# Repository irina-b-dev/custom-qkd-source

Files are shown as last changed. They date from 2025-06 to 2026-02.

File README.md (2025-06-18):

# custom-qkd-source

### On **Pi A** (set IP `192.168.2.1/24`):

Create a file:

```bash
sudo nano /etc/systemd/network/10-eth0.network
```

```ini
[Match]
Name=eth0

[Network]
Address=192.168.2.1/24
```

 Enable `systemd-networkd`:

```bash
sudo systemctl enable systemd-networkd
sudo systemctl restart systemd-networkd
```

Repeat similar steps on **Pi B**, but with a different address:

---

### On **Pi B** (set IP `192.168.2.2/24`):

```bash
sudo nano /etc/systemd/network/10-eth0.network
```

```ini
[Match]
Name=eth0

[Network]
Address=192.168.2.2/24
```

Then:

```bash
sudo systemctl enable systemd-networkd
sudo systemctl restart systemd-networkd
```

---

###  test:

```bash
ping 192.168.2.2  # from Pi A
ping 192.168.2.1  # from Pi B
```

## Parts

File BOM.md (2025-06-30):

## Optics

| Name                      | Link                                                                                                                                                 | Price   | Description                      | QTY | Code     | Check |
| ------------------------- | ---------------------------------------------------------------------------------------------------------------------------------------------------- | ------- | -------------------------------- | --- | -------- | ----- |
| Laser Detection card      | https://eksmaoptics.com/oem-dpss-lasers-diode-laser-modules/laser-accessories/laser-detection-cards/                                                 | 79 EUR  | 400-640 nm + 800-1700 nm         | 2   | 990-0846 | [x]   |
| Polarizing beam splitters | https://eksmaoptics.com/optical-components/polarizing-optics/cube-polarizing-beamsplitters/?listtype=search&searchparam=polarizing%20beam%20splitter | 135 EUR | 780nm Rs>99.5% Tp>95% 10 x 10 mm | 1   | 430-0102 | [x]   |
| BBO Crystal               | https://eksmaoptics.com/nonlinear-and-laser-crystals/nonlinear-crystals/beta-barium-borate-bbo-crystals-bbo-604h/                                    | 390 EUR | Type 1<br>P/P@400-800 nm         | 1   | BBO-604H | [x]   |
|                           |                                                                                                                                                      |         |                                  |     |          |       |

| Name                       | Link                                                                                       | Price   | Description                                        | Qty | Code | Check |
| -------------------------- | ------------------------------------------------------------------------------------------ | ------- | -------------------------------------------------- | --- | ---- | ----- |
| Safety Glasses             | https://www.edmundoptics.com/p/arg-lasershield-safety-comfort-glasses/41416/               | 141 EUR | D LB7 + IR LB4 @ 180-315nm, DIRM LB6 S @ 315-532nm | 1   |      | []    |
| IR Filter                  | https://www.edmundoptics.com/p/5mm-diameter-optical-cast-plastic-ir-longpass-filter/41541/ | 11 EUR  |                                                    | 2   |      | [x]   |
| Quarter Wave Plate<br><br> | https://www.edmundoptics.com/p/25mm-dia-4-retarder-film-wp140he/50157/                     | 16 EUR  | Polymer 25mm Dia., λ/4 Retarder Film               | 2   |      | [x]   |
| Half Wave Plate            | https://www.edmundoptics.com/p/25mm-dia-2-retarder-film-wp280/50160/                       | 16 EUR  | 25mm Dia., λ/2 Retarder Film                       | 2   |      | [x]   |
https://www.edmundoptics.com/Account/OrderHistory/Print/493222

| Name                 | Link                                                                             | Price   | Qty | Description                                                 | Code   | Check |
| -------------------- | -------------------------------------------------------------------------------- | ------- | --- | ----------------------------------------------------------- | ------ | ----- |
| 405nm Laser Diode    | https://ampul.eu/ro/diode-laser-module/2650-dioda-laser-405nm-20mw-diametru-56mm | 22,76 € | 3   | 405 nm, 20 mW, Ø5.6 mm, B Pin Code, Laser Diode             | AM2680 | [x]   |
| Alignemt laser 650nm | https://ampul.eu/en/laser-diodes-modules/2181-laser-module-5mw-650nm-dot         | 7.82 €  | 3   | Light color: Red<br>Wavelength: 650 nm<br>Performance: 5 mW | AM1232 | []    |
Total: 91 EUR
Needed (38 EUR)

| Name | Link                                                 | Price   | Qty | Description            | Code             | Check |
| ---- | ---------------------------------------------------- | ------- | --- | ---------------------- | ---------------- | ----- |
| APD  | https://ro.mouser.com/ProductDetail/193-MTAPD-06-001 | 37,21 € | 4   | Peak Wavelength: 800nm | 193-MTAPD-06-001 | [x]   |
Total : 184 EUR 
Needed (111.63 EUR)

For now
918 EUR Needed

## For Electronics (without APD and laser)

|                           |                         |           |                    |       |          |      |     |     |
| ------------------------- | ----------------------- | --------- | ------------------ | ----- | -------- | ---- | --- | --- |
| ---  --- |                         | For SPAD  |                    |       |          |      |     |     |
|                           |                         |           |                    |       |          |      |     |     |
| Ref.                      | Mfg.                    | Part No.  | Description        |       |          |      |     |     |
| APD                       | --                      | DAPD      | diode              |       |          |      |     |     |
| C1                        | --                      | --        | capacitor          | 33µF  | 2.7V     |      |     |     |
| C2                        | --                      | --        | capacitor          | 1µF   |          |      |     |     |
| C3                        | --                      | --        | capacitor          | 1µF   |          |      |     |     |
| C4                        | --                      | --        | capacitor          | 1µF   |          |      |     |     |
| C5                        | --                      | --        | capacitor          | 100nF |          |      |     |     |
| C6                        | --                      | --        | capacitor          | 10nF  |          |      |     |     |
| C7                        | --                      | --        | capacitor          | 100nF |          |      |     |     |
| C8                        | --                      | --        | capacitor          | 100nF |          |      |     |     |
| Cj                        | --                      | --        | capacitor          | 1pF   | 1KV      |      |     |     |
| Cn                        | --                      | --        | capacitor          | 10nF  |          |      |     |     |
| D1                        | OnSemi                  | 1N5818    | diode              |       |          |      |     |     |
| D2                        | OnSemi                  | 1N5819    | diode              |       |          |      |     |     |
| D3                        | Vishay                  | BAT54     | diode              |       |          |      |     |     |
| D4                        | Rohm                    | BAS21HY   | diode              |       |          |      |     |     |
| D5                        | Rohm                    | BAS21HY   | diode              |       |          |      |     |     |
| L1                        | --                      | --        | inductor           | 33µH  | 1.35A pk |      |     |     |
| M1                        | International Rectifier | IRF7832   | MOSFET             |       |          |      |     |     |
| M2                        | Siliconix               | Si7336ADP | MOSFET             |       |          |      |     |     |
| maboi                     | --                      | --        | resistor           | 1M    |          |      |     |     |
| R1                        | --                      | --        | resistor           | 1M    | 1.00%    | 0.1W |     |     |
| R2                        | --                      | --        | resistor           | 100K  |          |      |     |     |
| R3                        | --                      | --        | resistor           | 49.9K |          |      |     |     |
| R4                        | --                      | --        | resistor           | 6.8K  |          |      |     |     |
| R5                        | --                      | --        | resistor           | 20K   |          |      |     |     |
| R6                        | --                      | --        | resistor           | 300   |          |      |     |     |
| R7                        | --                      | --        | resistor           | 1K    |          |      |     |     |
| R8                        | --                      | --        | resistor           | 1.9K  |          |      |     |     |
| R9                        | --                      | --        | resistor           | 6K    |          |      |     |     |
| R10                       | --                      | --        | resistor           | 500K  |          |      |     |     |
| R11                       | --                      | --        | resistor           | 1K    |          |      |     |     |
| R13                       | --                      | --        | resistor           | 150K  |          |      |     |     |
| Rbias                     | --                      | --        | resistor           | 14K   |          |      |     |     |
| Rbias1                    | --                      | --        | resistor           | 10K   |          |      |     |     |
| Rdivider                  | --                      | --        | resistor           | 140K  |          |      |     |     |
| Rdrain                    | --                      | --        | resistor           | 90K   |          |      |     |     |
| Re0                       | --                      | --        | resistor           | 10    |          |      |     |     |
| Ri                        | --                      | --        | resistor           | 200K  |          |      |     |     |
| Rth                       | --                      | --        | resistor           | 1M    |          |      |     |     |
| U1                        | Analog Devices          | LT1172    | integrated circuit |       |          |      |     |     |
| U2                        | Analog Devices          | LT1711    | integrated circuit |       |          |      |     |     |
| U3                        | Analog Devices          | AD8605    | integrated circuit |       |          |      |     |     |
|                           |                         |           |                    |       |          |      |     |     |

For Laser Driver

| Reference | Value          | Datasheet                                                                                                     | Footprint                    | Qty |
| --------- | -------------- | ------------------------------------------------------------------------------------------------------------- | ---------------------------- | --- |
| A1        | SC0918         | https://datasheets.raspberrypi.com/picow/pico-w-datasheet.pdf                                                 | Raspberry Pi:MODULE_SC0918   | 1   |
| D1        | BZV55B3V6      | https://assets.nexperia.com/documents/data-sheet/BZV55_SER.pdf                                                | Diode_SMD:D_MiniMELF         | 1   |
| IC1       | UCC27531DBVT   | http://www.ti.com/lit/ds/symlink/ucc27531.pdf                                                                 | MyMegaLib:SOT95P280X145-6N   | 1   |
| LD1       | PLT5_510       | https://look.ams-osram.com/m/2562f8ca3a03a793/original/PLT5-510.pdf                                           | OptoDevice:LaserDiode_TO56-3 | 1   |
| Q1        | BSC123N08NS3_G | https://www.infineon.com/dgdl/Infineon-BSC123N08NS3G-DS-v02_05-en.pdf?fileId=db3a30431add1d95011ae80eb8555625 | MyMegaLib:PG-TDSON-8         | 1   |
| R1,R2     | 5              | ~                                                                                                             |                              | 2   |
| R3        | 300            | ~                                                                                                             |                              | 1   |
|           |                |                                                                                                               |                              |     |

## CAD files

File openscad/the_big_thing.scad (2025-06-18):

use <scad-lib-FDMscrews-main/lib-FDMscrews.scad>


width = 53.8;
depth = 81.5;
height = 9.5;

rail_width = 9;
center_width = width - 2*rail_width;

r_width = 3.4;
r_depth = 1.5;
r_height = 4.3;
r_dist = 49.5;
r_dist1 = (depth - r_dist)/2;


pico_depth = 52.6;
pico_width = 21.1;
pico_height = 19 - height;


//cube([width, depth, height]);

$fn = 100; // smooth thread

pitch = 2;



////////////////////////////////////////////////////

// module stuff(d_outer=20, pitch=2, length=12, inner=12.7){
//      screwByPitch(pitch=pitch,
//                      d0=d_outer,
//                      dr=1.5,
//                      length=length,
//                      flat=1);

//         translate([0, 0, length])
//         screwByPitch(pitch=pitch,
//                      d0=25.6 + 8,
//                      dr=1.5,
//                      length=length,
//                      flat=1);
//             //cylinder(d=25.5 + 3, h=length + 2, center=false, $fn=$fn);
// }


// module stuff2(d_outer=20, pitch=2, length=12, inner=12.7){
//      screwByPitch(pitch=pitch,
//                      d0=d_outer,
//                      dr=1.5,
//                      length=length,
//                      flat=1);

//         translate([0, 0, length])
//         screwByPitch(pitch=pitch,
//                      d0=25.6 + 8.4,
//                      dr=1.5,
//                      length=length,
//                      flat=1);
//             //cylinder(d=25.5 + 3, h=length + 2, center=false, $fn=$fn);
// }


// module hollow_screw(d_outer=20, pitch=2, length=12, inner=12.7) {
 

//    difference(){

//         {
//             stuff();
//         }

//         color([1,0,0]){
        
//          translate([0, 0, 0])
//             cylinder(d=inner, h=length + 23, center=false, $fn=$fn);
        
//         translate([0, 0, length + 3])
//             cylinder(d=25.6 + 2, h=length, center=false, $fn=$fn);

//         }

//    }
     
// }

// module cap(d_outer=20, pitch=2, length=12, inner=12.7){
//     translate([0,0,length+1.5])
//         cylinder(d=25.6 + 8 + 5, h=length + 2, center=false, $fn=$fn);
// }

// module hollow_screw_cap(d_outer=20, pitch=2, length=8, inner=12.7){
//    difference(){
        
//         cap();
//         {
//         stuff2();

//         translate([0, 0, 0])
//             cylinder(d=inner + 5, h=length + 23, center=false, $fn=$fn);
//         }

//    }
// }
///////////////////////////////////////////////////////////////////////


//do = 25.6;
do = 25;

module stuff(d_outer=20, pitch=2, length=8, inner=12.7){
    translate([0, 0, -4])
     screwByPitch(pitch=pitch,
                     d0=d_outer,
                     dr=1.5,
                     length=length + 4,
                     flat=1);

        translate([0, 0, length])
        screwByPitch(pitch=pitch,
                     d0=do + 8,
                     dr=1.5,
                     length=length,
                     flat=1);
            //cylinder(d=25.5 + 3, h=length + 2, center=false, $fn=$fn);
}

allowance = 0.7;
module stuff2(d_outer=20, pitch=2, length=8, inner=12.7){
     screwByPitch(pitch=pitch,
                     d0=d_outer + allowance,
                     dr=1.5,
                     length=length,
                     flat=1);

        translate([0, 0, length])
        screwByPitch(pitch=pitch,
                     d0=do + 8 + allowance,
                     dr=1.5,
                     length=length,
                     flat=1);
            //cylinder(d=25.5 + 3, h=length + 2, center=false, $fn=$fn);
}


module hollow_screw(d_outer=20, pitch=2, length=8, inner=12.7) {
 

   difference(){

        {
            stuff();
        }

        color([1,0,0]){
        
         translate([0, 0, -4])
            cylinder(d=inner, h=length + 23, center=false, $fn=$fn);
        
        translate([0, 0, length + 3])
            cylinder(d=do + 2, h=length, center=false, $fn=$fn);

        }

   }
     
}

module cap(d_outer=20, pitch=2, length=8, inner=12.7){
    translate([0,0,length+1.5 - 4])
        cylinder(d=do + 8 + 5, h=length + 6, center=false, $fn=$fn);
}
module cap_inferior(d_outer=20, pitch=2, length=8, inner=12.7){
    translate([0,0,length*2])
        cylinder(d=d_outer + 5, h=length + 2, center=false, $fn=$fn);
}

module hollow_screw_cap(d_outer=20, pitch=2, length=8, inner=12.7){
   difference(){
        
        cap();
        {
        translate([0,0,-3])
        stuff2();

        translate([0, 0, 0])
            cylinder(d=inner + 5, h=length + 23, center=false, $fn=$fn);
        }

   }



     difference(){
        
        cap_inferior();
        {
        translate([0,0,length*2 + 4])
        stuff2();

         translate([0, 0, length*2])
            cylinder(d=inner + 5, h=length + 23, center=false, $fn=$fn);
        }

   }
}














waveplate_d = 25;
waveplate_h = 0.053;

fit_clearance = 0.2;
holder_d = waveplate_d + fit_clearance;
holder_h = 5;
pocket_d = holder_d;
pocket_h = waveplate_h + 0.05;

lip_h = 0.5;
lip_t = 0.5;

//$fn = 100; // smooth cylinder

module waveplate_holder() {
    difference() {
        // Outer body of the holder
        cylinder(d=holder_d + 2, h=holder_h);

        // Pocket to hold the waveplate
        translate([0, 0, 0 ])
         cylinder(d=holder_d, h=holder_h);

        // Optional central hole if you want to reduce material
        // translate([0, 0, 0]) cylinder(d=10, h=holder_h);
    }

    // // Optional lip to hold the waveplate from above
    // translate([0, 0, holder_h])
    //     cylinder(d=holder_d, h=lip_h);

    // Optional: Add mounting holes or features here
}





module pico_board(){
    color([0,0.7,0])
    cube([pico_width, pico_depth, pico_height]);
}

module breadboard_piece(wdt = rail_width, dth = depth){

    difference(){ 

        cube([wdt, dth, height]);
        {
            translate([wdt/2 - r_width/2, dth - r_depth, 0])
            cube([r_width, r_depth, r_height]);

            translate([0,  r_dist1- r_width/2, 0])
            cube([r_depth, r_width, r_height]);

            translate([0,  dth- r_dist1 + r_width/2, 0])
            cube([r_depth, r_width, r_height]);
        }

        
    }
    
    translate([wdt/2 - r_width/2, -r_depth, 0])
    cube([r_width, r_depth, r_height]);

    translate([wdt,  r_dist1 - r_width/2, 0])
    cube([r_depth, r_width, r_height]);

    translate([wdt,  dth - r_dist1 + r_width/2, 0])
    cube([r_depth, r_width, r_height]);
}

module breadboard_middle(){
    breadboard_piece(wdt=center_width);
}


module breadboard(){
    
    // cube([center_width, depth, height]);
    breadboard_piece(wdt=center_width);

    translate([-rail_width, 0, 0])
    color([1, 0, 1])
    breadboard_piece();

    translate([center_width, 0, 0])
    color([1, 0, 0])
    breadboard_piece();
    
    }

module double_breadboard(){

    breadboard_piece(wdt=center_width);

    translate([center_width, 0, 0])
    breadboard_piece(wdt=center_width);


    translate([-rail_width, 0, 0])
    color([0, 0, 1])
    breadboard_piece();

    translate([center_width*2, 0, 0])
    color([1, 0, 0])
    breadboard_piece();

}


bbo_diameter = 25.4;

module bbo_ring(){
    difference() {
    // Outer cylinder
    cylinder(d=bbo_diameter, h=3, $fn=100);  // $fn = smoothness (100 segments)

    // Inner cylinder (hole)
    cylinder(d=bbo_diameter - 2*2, h=3, $fn=100);  // 2 mm wall on both sides
}

}

module spad(apd_pos = 0, h_ray){
    breadboard_piece(wdt=center_width);
    translationx = (apd_pos == 0) ? center_width * 0.80 :
                   (apd_pos == 1) ? center_width * 0.27 - apd_size/2 :
                   (apd_pos == 2) ? center_width * 0.77 - apd_size :
                   "unknown";  // fallback
    translate([translationx, depth - depth/4 , height])
    apd(h_ray = h_ray);
}


module pico_on_board(){
    breadboard_piece(wdt=center_width);
    translate([width/8,depth/8,height])
    pico_board();
}

module spad_module(apd_pos = 0, h_ray){
    spad(apd_pos, h_ray);
    translate([-center_width, 0,0])
    pico_on_board();
}


ray_dim_d = 6;
beam_splitter_dim = 10;
beam_splitter_dist = 20;
module beam_splitter(){

    
     //ray straight
    // color([0.7,0,0,0.6])
    // translate([beam_splitter_dim/2 - ray_dim_d/2, -beam_splitter_dist , beam_splitter_dim/2 - ray_dim_d/4])
    // rotate([90,0,0])
    // mirror([0,0,1])
    // cylinder(d=ray_dim_d, h= 25, $fn=100);

    // //ray pol

    // color([0.7,0,0,0.6])
    // translate([beam_splitter_dim/2 - ray_dim_d/2, beam_splitter_dim/2- ray_dim_d/2 , beam_splitter_dim/2 - ray_dim_d/4])
    // rotate([0,90,0])
    // cylinder(d=ray_dim_d, h= 25, $fn=100);


    color([0,1,0,0.5])
    cube([beam_splitter_dim, beam_splitter_dim, beam_splitter_dim]);

   


    
}

filter_size = 5;
module filter(){

    cylinder(d=filter_size, h=3, $fn=100);  // $fn = smoothness (100 segments)
}



apd_size = 3.2;
module apd(h_ray = 100){
    color([0.1,0,0.1,1])
    cylinder(d=apd_size, h=apd_size, $fn=100);
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

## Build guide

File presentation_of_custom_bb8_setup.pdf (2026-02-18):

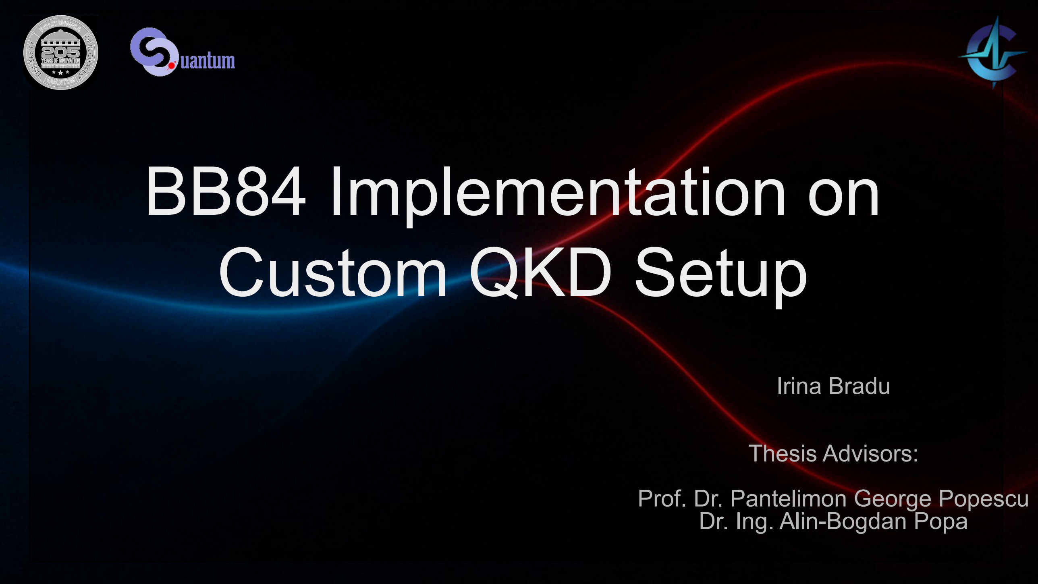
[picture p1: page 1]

# BB84 Implementation on Custom QKD Setup

## Irina Bradu

## Thesis Advisors:

## Prof. Dr. Pantelimon George Popescu Dr. Ing. Alin-Bogdan Popa

# Motivation

## - Educational outreach

## - Hardware experimentation

## - Cost constraints

BB84 Implementation on custom QKD setup - Irina Bradu - June 2025 | 2

# BB84 recap

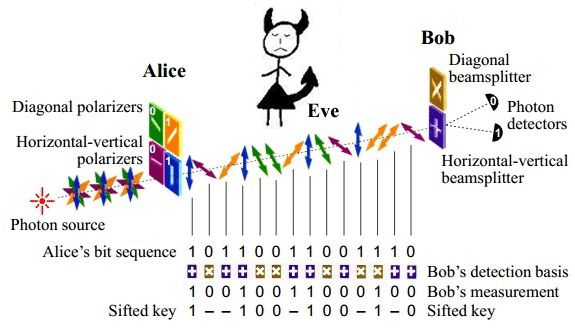
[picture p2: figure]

Credit : Weerasinghe, WAA Maheshya. "Quantum Cryptography." (2012).

BB84 Implementation on custom QKD setup - Irina Bradu - June 2025 | 3

# Overview of the setup

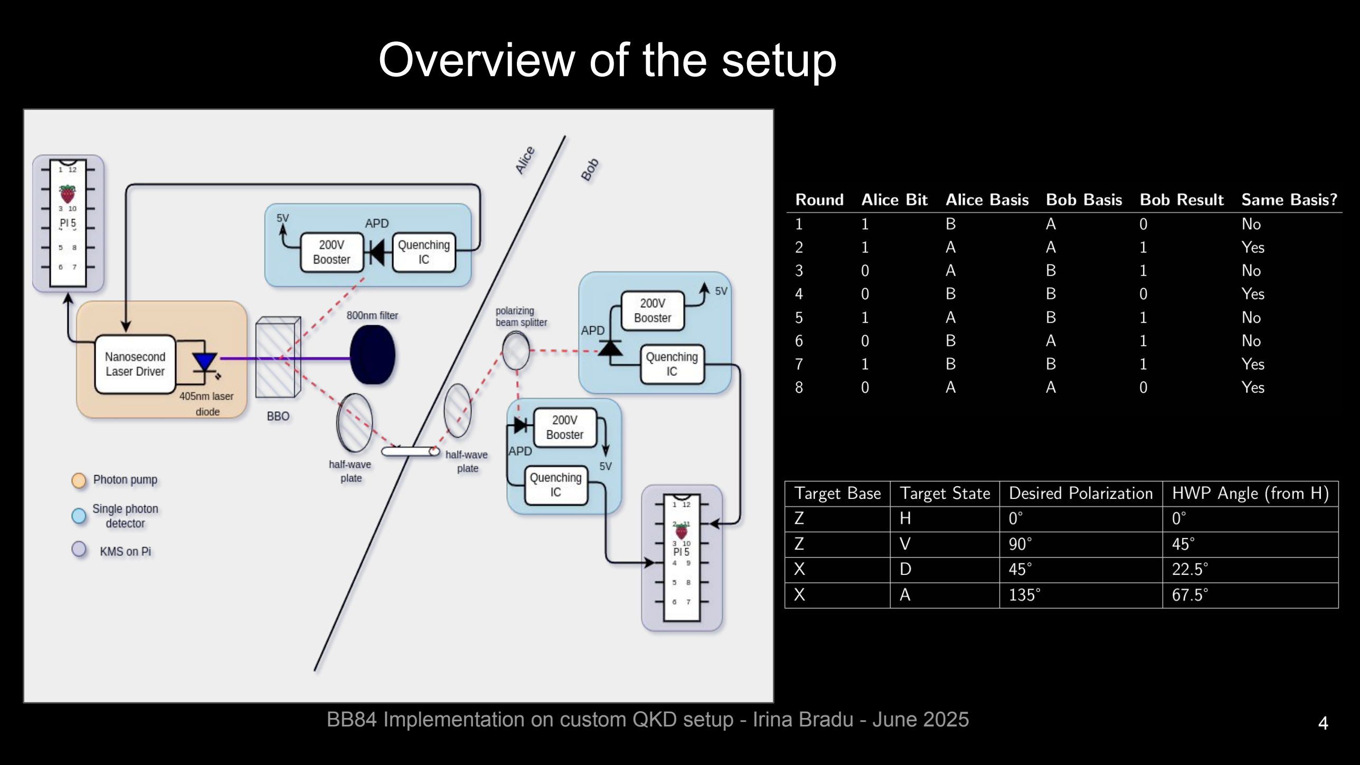
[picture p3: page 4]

BB84 Implementation on custom QKD setup - Irina Bradu - June 2025 | 4

# 3D design

## Alice

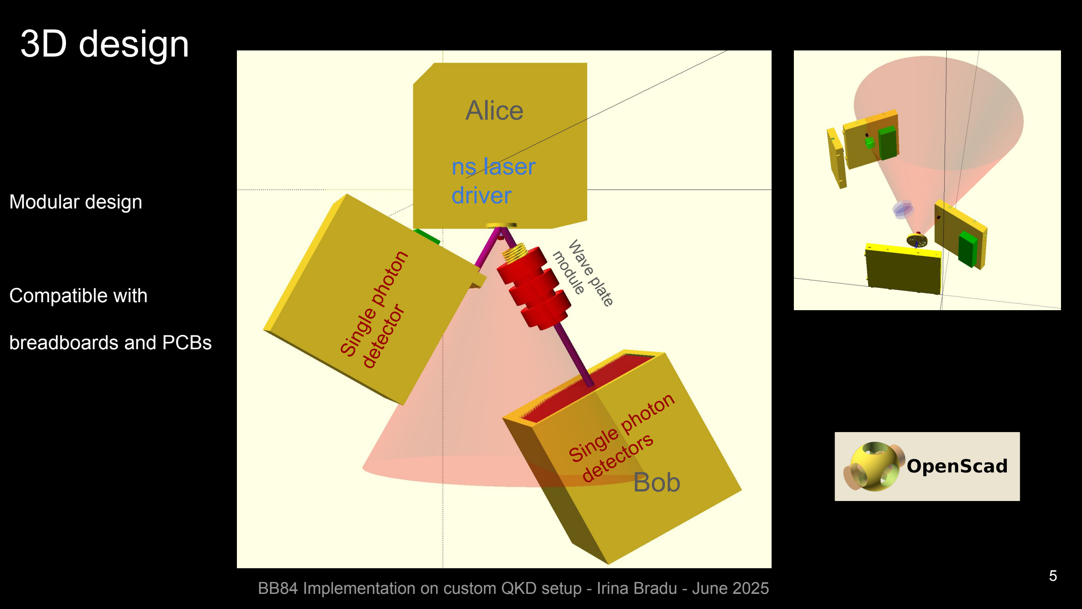
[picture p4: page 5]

## Bob

## ns laser driver

Wave plate
module

Single photon

detector

## Single photon

## detectors

- Modular design
- Compatible with

breadboards and PCBs

5
BB84 Implementation on custom QKD setup - Irina Bradu - June 2025

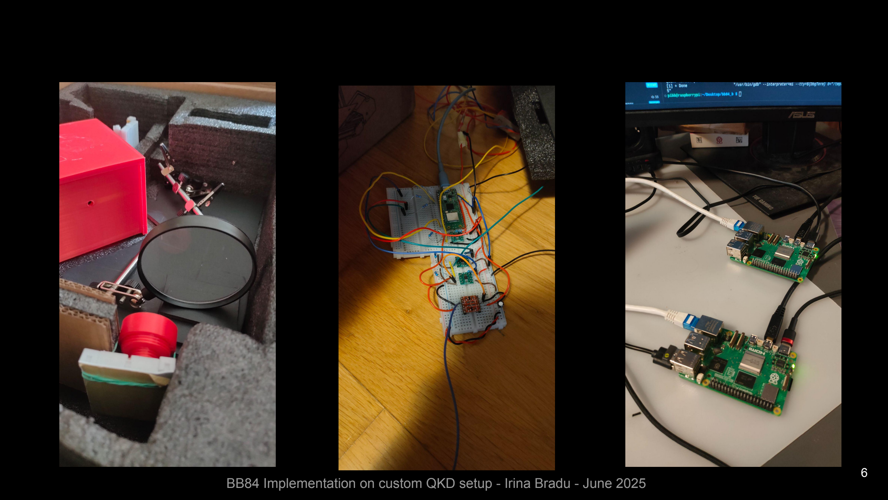
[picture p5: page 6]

6
BB84 Implementation on custom QKD setup - Irina Bradu - June 2025

# Hardware Design

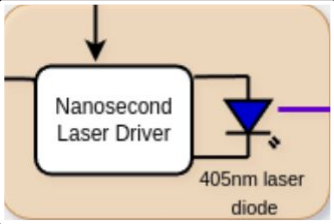
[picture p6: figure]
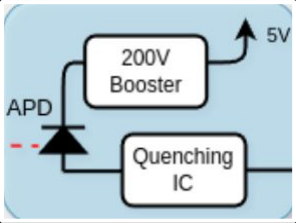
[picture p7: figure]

1 | 2

3

BB84 Implementation on custom QKD setup - Irina Bradu - June 2025 | 7

# Hardware Design of the LASER driver

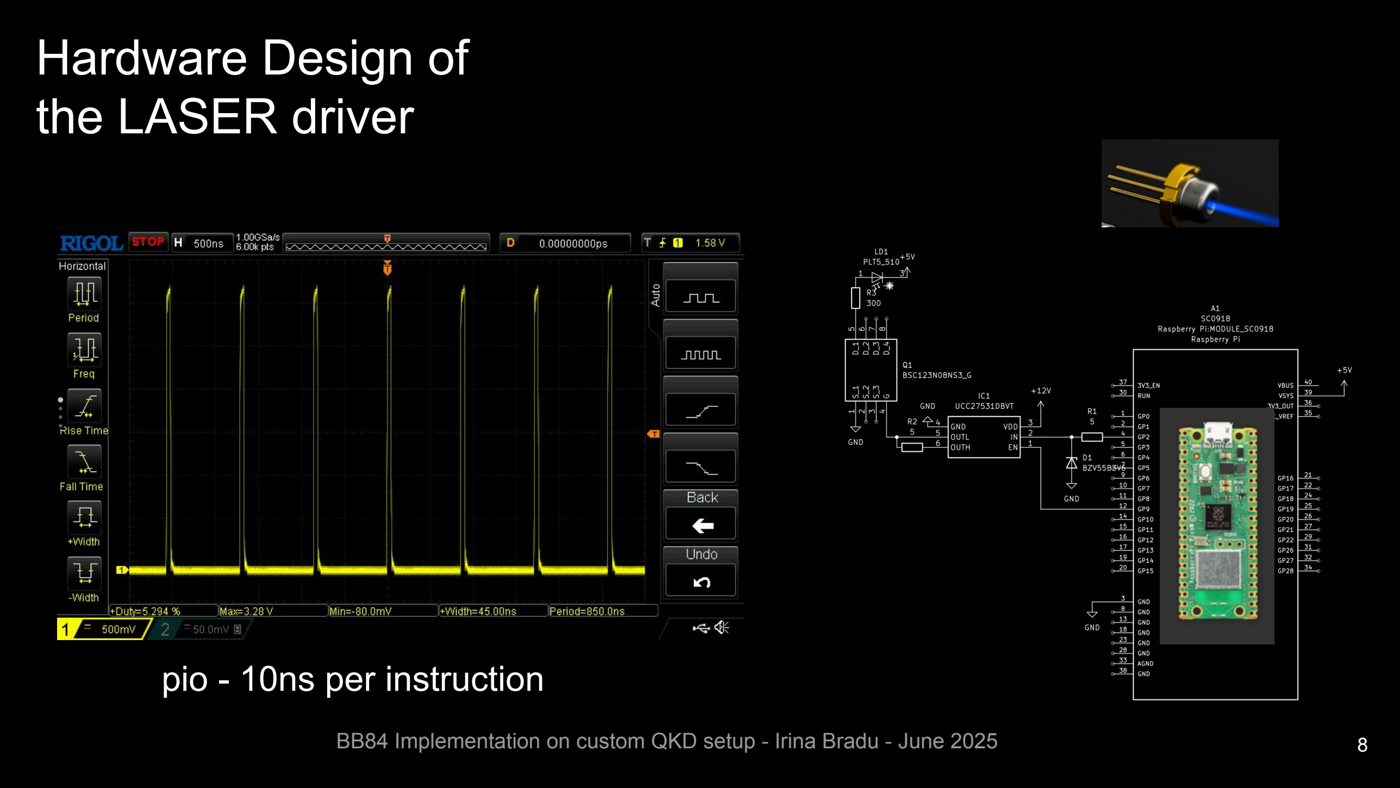
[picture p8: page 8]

## pio - 10ns per instruction

BB84 Implementation on custom QKD setup - Irina Bradu - June 2025 | 8

# Hardware Design of the 5V to 200V Boost Converter

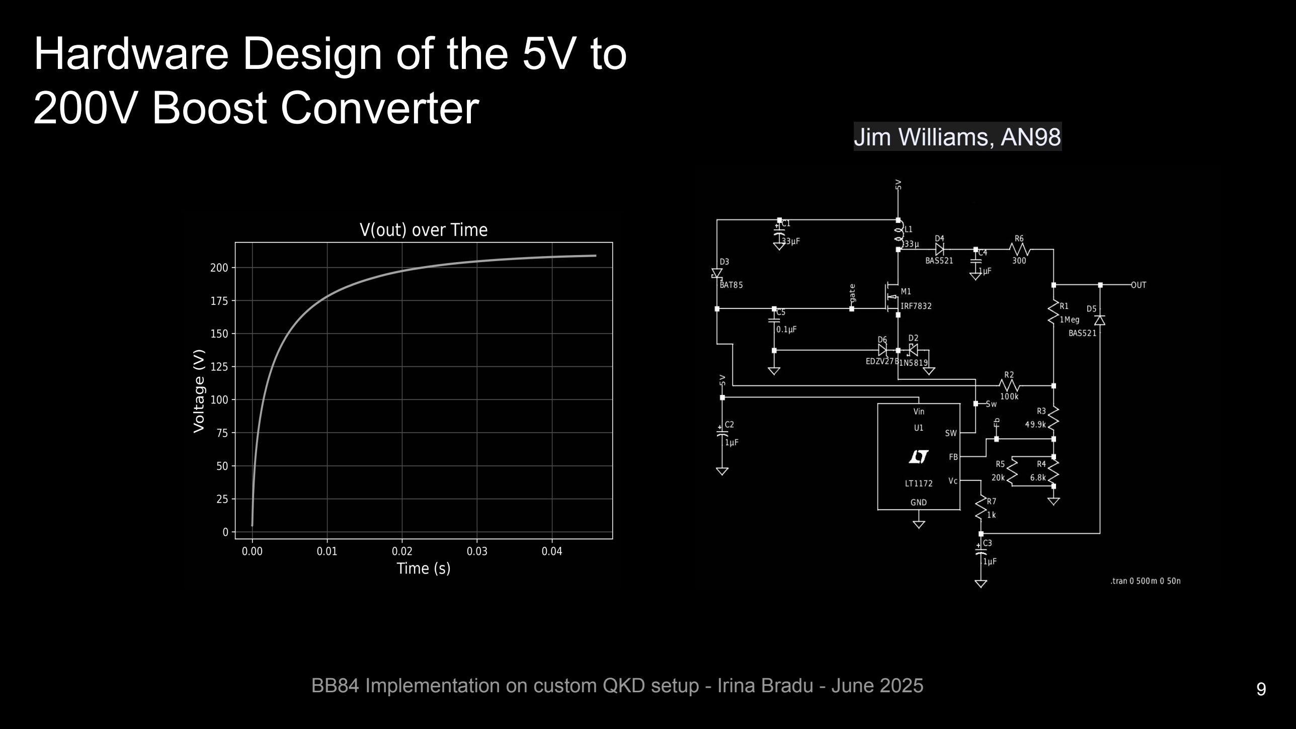
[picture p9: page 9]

BB84 Implementation on custom QKD setup - Irina Bradu - June 2025 | 9

### Jim Williams, AN98

# Hardware Design of the Adjustable Boost Converter

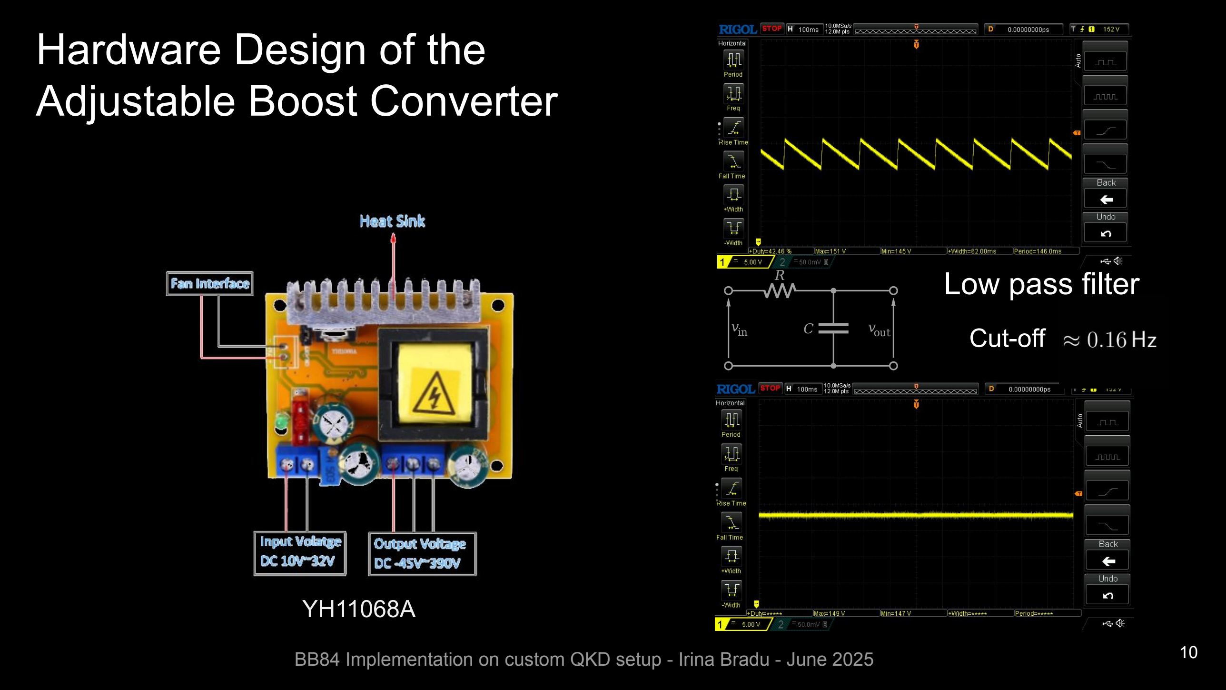
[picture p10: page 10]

## Cut-off

## Low pass filter

10 BB84 Implementation on custom QKD setup - Irina Bradu - June 2025

### YH11068A

# Hardware Design of the Single Photon Detector with Active

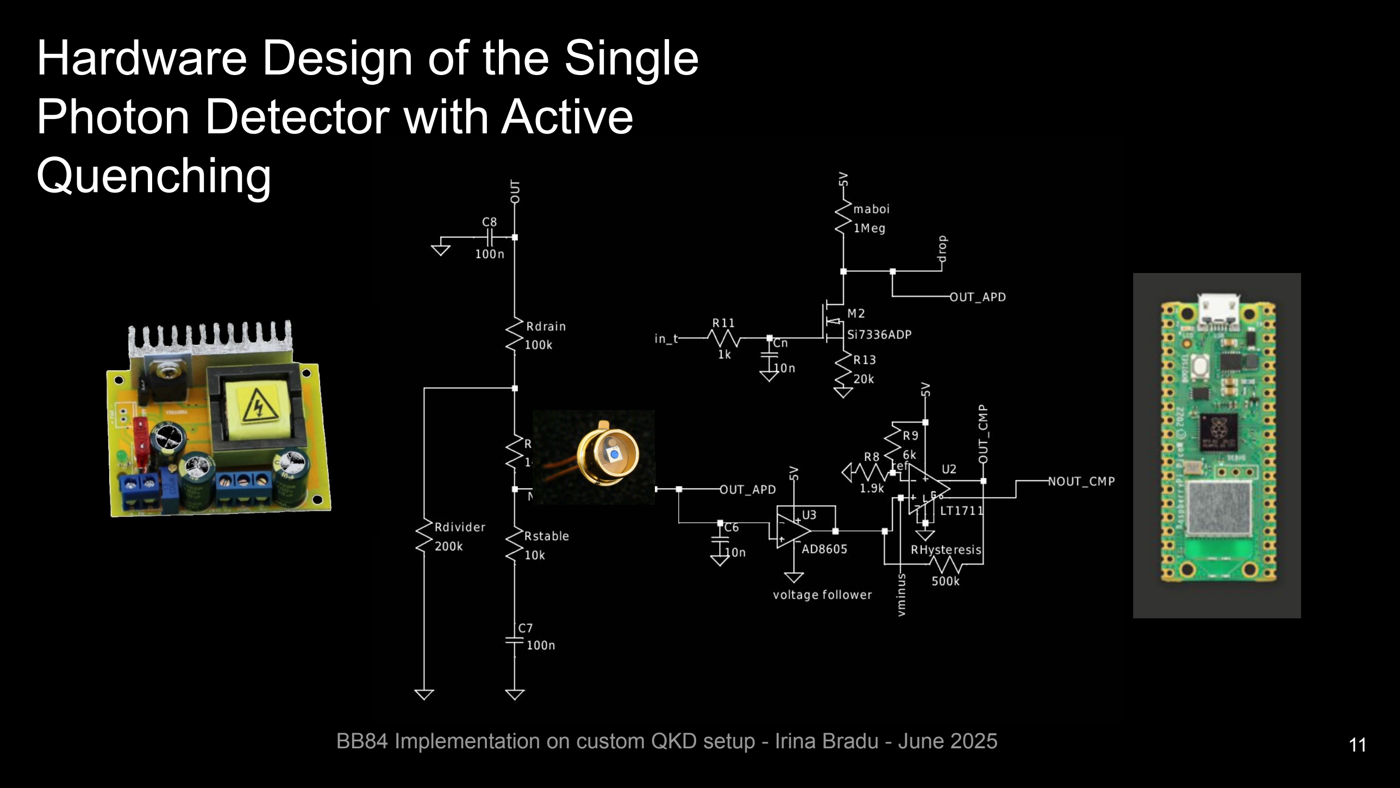
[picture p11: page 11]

# Quenching

BB84 Implementation on custom QKD setup - Irina Bradu - June 2025 | 11

# Optics and alignment considerations

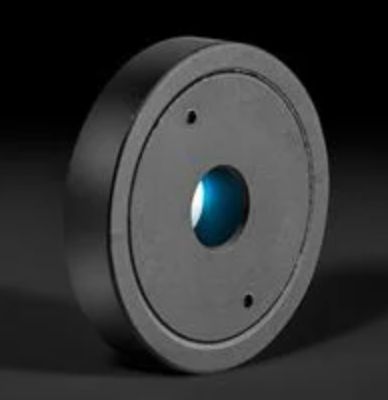
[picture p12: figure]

BBO crystal -
Type 1 SPDC

P/P@400-800
nm

Creating single
photons

Changing photon state
and measurement basis

Redirecting the photons depending

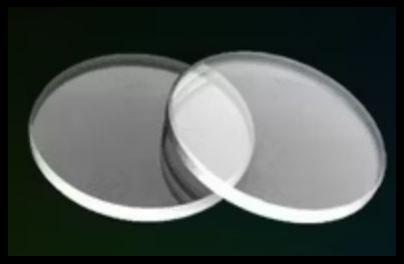
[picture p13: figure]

Half-wave plates

25mm Dia., λ/2
Retarder Film

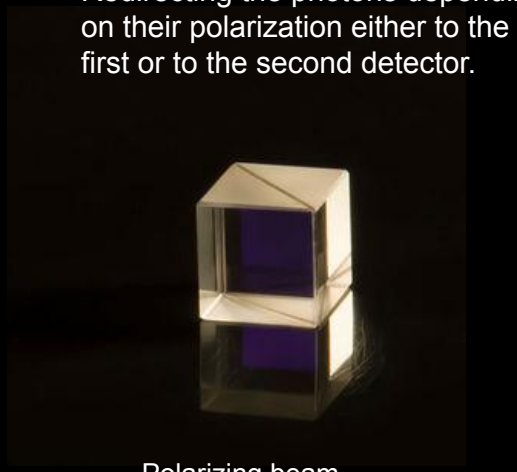
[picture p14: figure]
on their polarization either to the first or to the second detector.

Polarizing beam
splitter

780nm Rs>99.5%
Tp>95% 10 x 10 mm
BB84 Implementation on custom QKD setup - Irina Bradu - June 2025 | 12

# The software

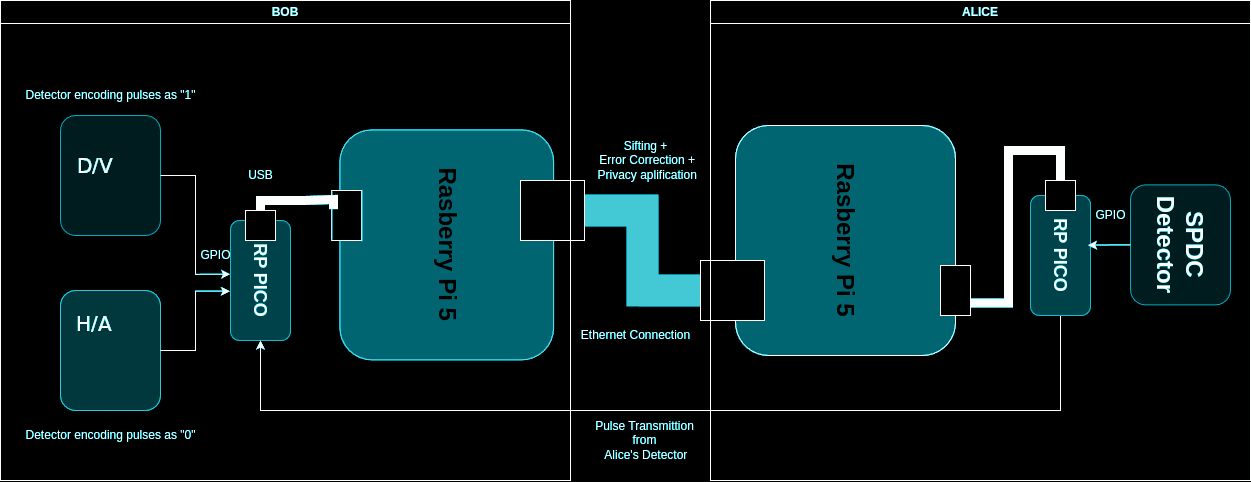
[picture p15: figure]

BB84 Implementation on custom QKD setup - Irina Bradu - June 2025 | 13

# The software

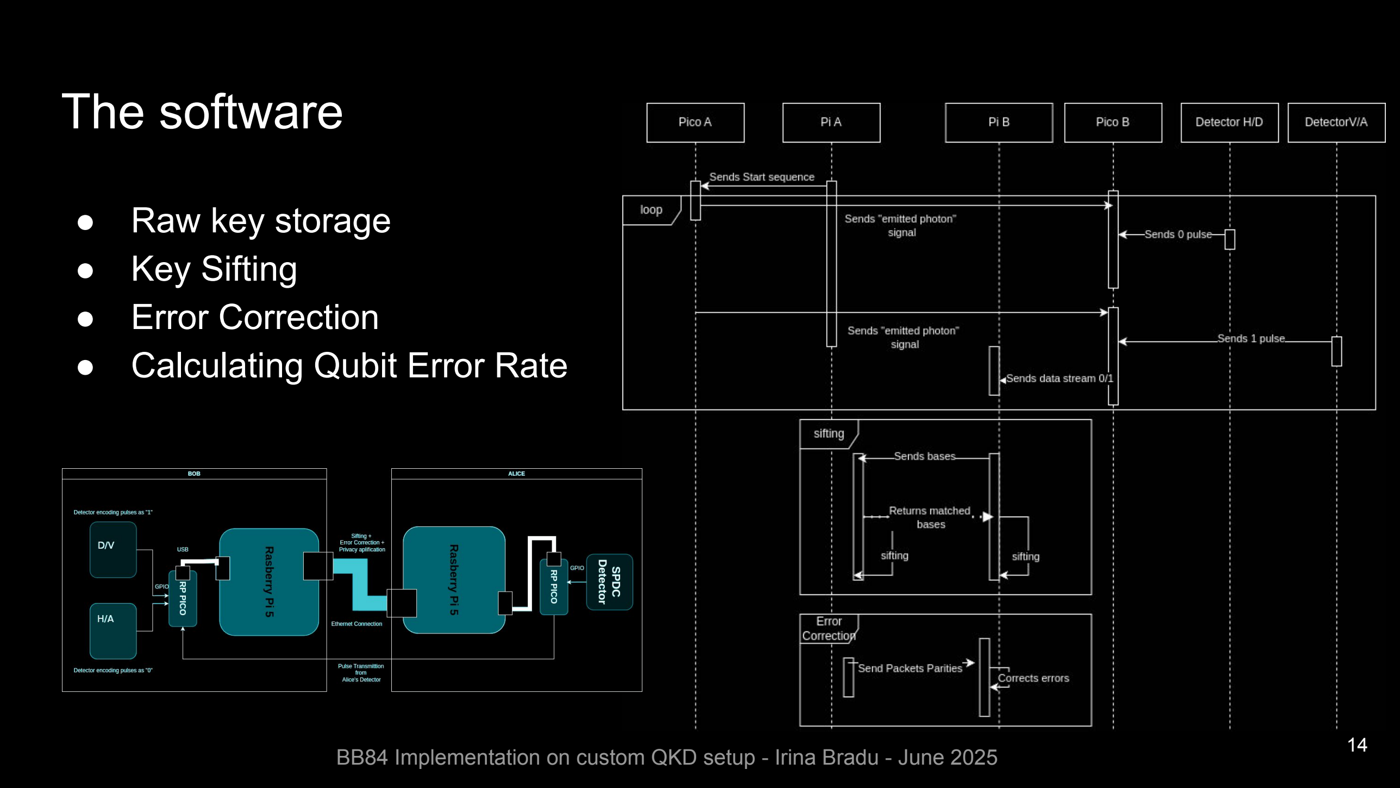
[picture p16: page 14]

## - Raw key storage - Key Sifting - Error Correction - Calculating Qubit Error Rate

14 BB84 Implementation on custom QKD setup - Irina Bradu - June 2025

# Results

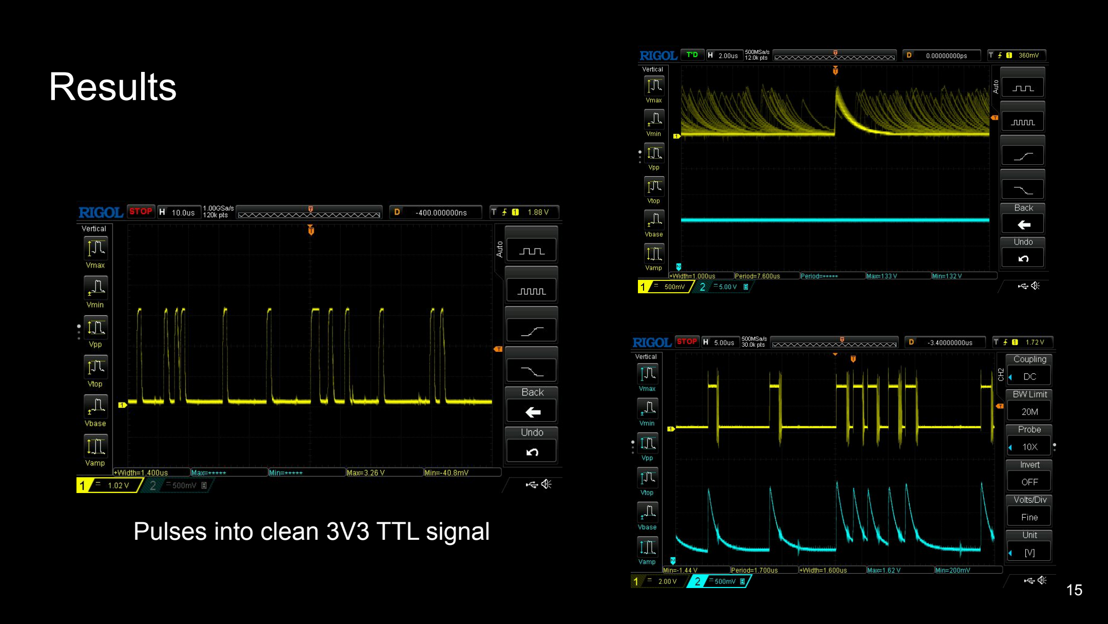
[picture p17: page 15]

15

## Pulses into clean 3V3 TTL signal

# Results

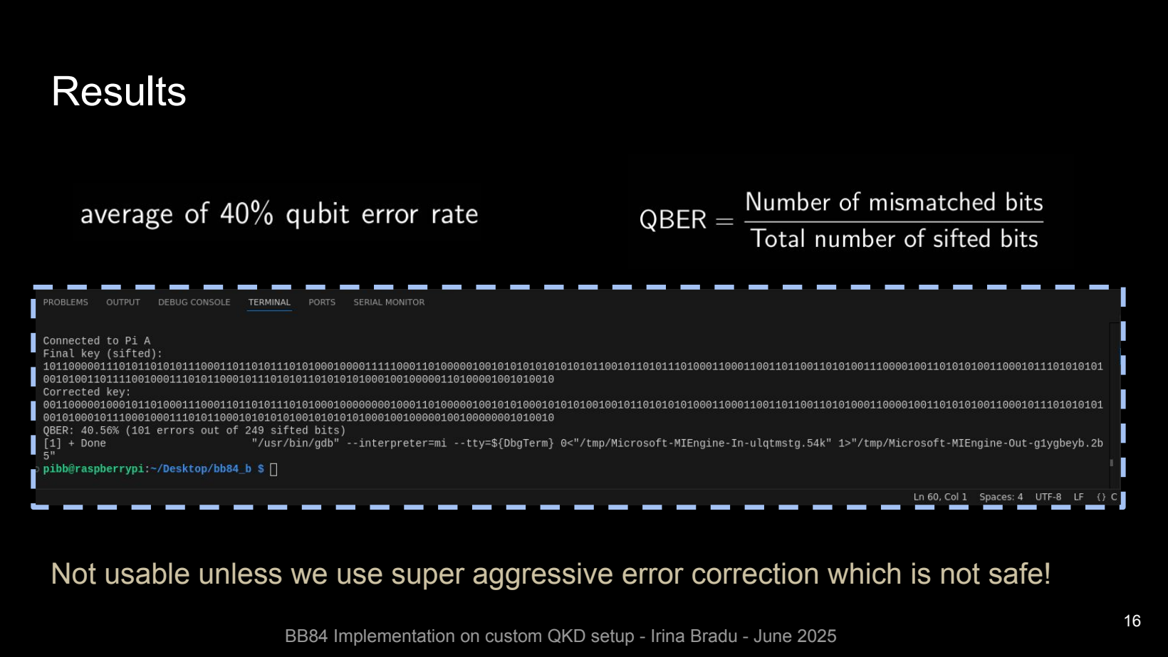
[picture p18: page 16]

## Not usable unless we use super aggressive error correction which is not safe!

16
BB84 Implementation on custom QKD setup - Irina Bradu - June 2025

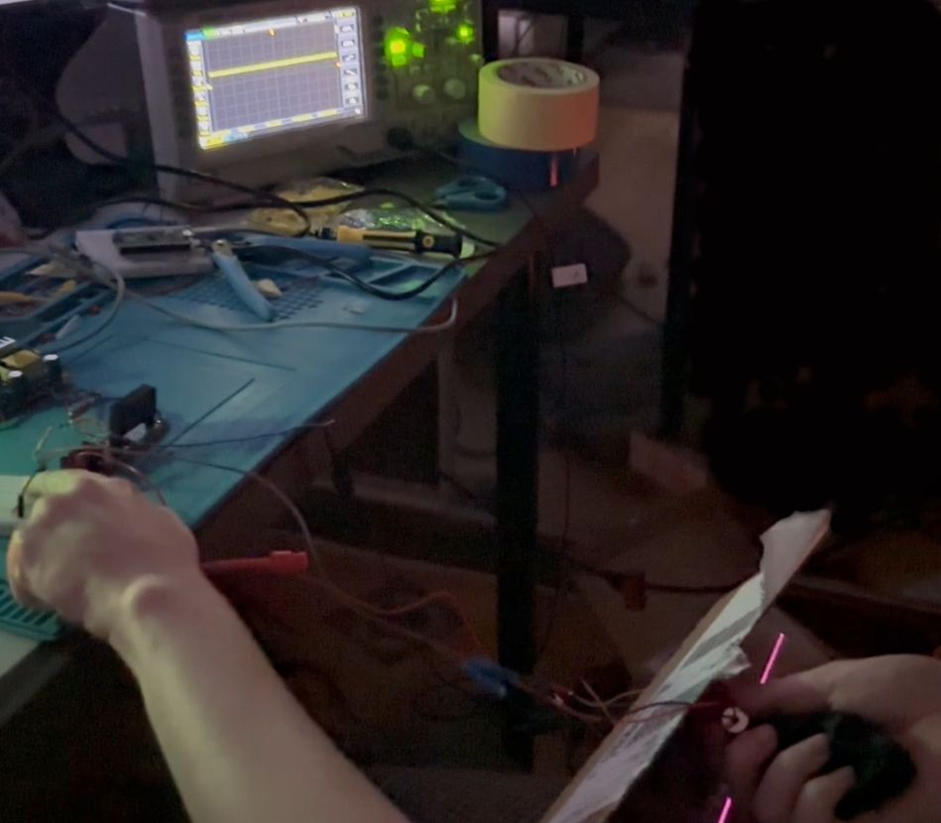
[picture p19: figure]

BB84 Implementation on custom QKD setup - Irina Bradu - June 2025 | 17

# Future work

## - Noise reduction -> Cooling

## - Better single photon generation -> Refining optical alignment

## - Higher photon detection rate -> Use SiPM (silicon photomultiplier)

BB84 Implementation on custom QKD setup - Irina Bradu - June 2025 | 18

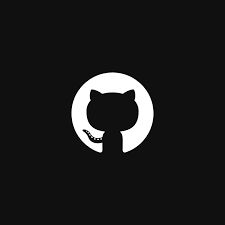
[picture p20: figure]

## https://github.com/irina-b-dev/custom-qkd-source

19

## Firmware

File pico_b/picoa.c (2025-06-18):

// #include <stdio.h>

// #include "pico/stdlib.h"
// #include "hardware/pio.h"

// #include "pulse_detect.pio.h"

// #define ZERO_PIN 2
// #define ONE_PIN 3

// void setup_pio_input(PIO pio, uint sm, uint offset, uint pin) {
//     pio_sm_config c = detect_pulse_program_get_default_config(offset);
//     pio_sm_set_consecutive_pindirs(pio, sm, pin, 1, false);
//     pio_gpio_init(pio, pin);
//     sm_config_set_in_pins(&c, pin);
//     sm_config_set_fifo_join(&c, PIO_FIFO_JOIN_RX);
//     sm_config_set_clkdiv(&c, 1.0f);  // full speed
//     pio_sm_init(pio, sm, offset, &c);
//     pio_sm_set_enabled(pio, sm, true);
// }

// // void setup_pio_input(PIO pio, uint sm, uint offset, uint pin) {
// //     pio_sm_config c = detect_pulse_program_get_default_config(offset);

// //     // Configure pins 2, 3, 4 as inputs (so pin 4 can be read by PIO)
// //     pio_sm_set_consecutive_pindirs(pio, sm, 4, 1, false);
// //     for (int i = pin; i < pin + 3; i++) {
// //         pio_gpio_init(pio, i);
// //     }

// //     sm_config_set_in_pins(&c, 4);  // base pin for 'in pins' instruction (pin 2 or 3)
// //     sm_config_set_fifo_join(&c, PIO_FIFO_JOIN_RX);
// //     sm_config_set_clkdiv(&c, 1.0f);  // full speed

// //     pio_sm_init(pio, sm, offset, &c);
// //     pio_sm_set_enabled(pio, sm, true);
// // }


// void setup_pio_input(PIO pio, uint sm, uint offset, uint pulse_pin, uint gate_pin) {
//     pio_sm_config c = detect_pulse_program_get_default_config(offset);

//     // Initialize both pins
//     gpio_init(pulse_pin);
//     gpio_init(gate_pin);
//     gpio_set_dir(gate_pin, GPIO_IN);
//     gpio_pull_down(gate_pin);  // or _up based on logic level

//     // Configure both pins as inputs for PIO
//     pio_gpio_init(pio, pulse_pin);
//     pio_gpio_init(pio, gate_pin);
//     pio_sm_set_consecutive_pindirs(pio, sm, pulse_pin, 1, false);
//     pio_sm_set_consecutive_pindirs(pio, sm, gate_pin, 1, false);

//     // Set base pin to gate pin so `jmp pin` uses it
//     sm_config_set_in_pins(&c, gate_pin);

//     sm_config_set_fifo_join(&c, PIO_FIFO_JOIN_RX);
//     sm_config_set_clkdiv(&c, 1.0f);

//     pio_sm_init(pio, sm, offset, &c);
//     pio_sm_set_enabled(pio, sm, true);
// }



// int main() {
//     stdio_init_all();

//     // gpio_init(4);
//     // gpio_set_dir(4, GPIO_IN);

//     // gpio_pull_down(4);  // or gpio_pull_up(4); based on your wiring



//     PIO pio = pio0;
//     uint offset = pio_add_program(pio, &detect_pulse_program);

//     uint sm_zero = 0;
//     uint sm_one  = 1;

//     setup_pio_input(pio, sm_zero, offset, ZERO_PIN, 4);
//     setup_pio_input(pio, sm_one, offset, ONE_PIN, 4);

//     //  setup_pio_input(pio, sm_zero, offset, ZERO_PIN);
//     // setup_pio_input(pio, sm_one, offset, ONE_PIN);

//     while (true) {
//         if (!pio_sm_is_rx_fifo_empty(pio, sm_zero)) {
//             pio_sm_get_blocking(pio, sm_zero);
//             printf("0");
//         }
//         if (!pio_sm_is_rx_fifo_empty(pio, sm_one)) {
//             pio_sm_get_blocking(pio, sm_one);
//             printf("1");
//         }
//     }
// }


#include <stdio.h>
#include "pico/stdlib.h"
#include "hardware/pio.h"
#include "pulse_detect.pio.h"

#define ZERO_PIN 4  // Pulse 0
#define ONE_PIN  5  // Pulse 1
#define GATE0_PIN 2 // Gate for Pulse 0
#define GATE1_PIN 3 // Gate for Pulse 1

void setup_pio_input(PIO pio, uint sm, uint offset, uint pulse_pin, uint gate_pin) {
    pio_sm_config c = detect_pulse_program_get_default_config(offset);

    // Initialize pins
    gpio_init(pulse_pin);
    gpio_init(gate_pin);
    gpio_set_dir(pulse_pin, GPIO_IN);
    gpio_set_dir(gate_pin, GPIO_IN);
    gpio_pull_down(pulse_pin);
    gpio_pull_down(gate_pin);

    // PIO needs both pulse and gate pin initialized
    pio_gpio_init(pio, pulse_pin);
    pio_gpio_init(pio, gate_pin);

    // Base pin is pulse_pin, and we assume gate_pin = pulse_pin + 2
    sm_config_set_in_pins(&c, pulse_pin);
    pio_sm_set_consecutive_pindirs(pio, sm, pulse_pin, 3, false);  // Covers pulse, (pulse+1), gate

    sm_config_set_fifo_join(&c, PIO_FIFO_JOIN_RX);
    sm_config_set_clkdiv(&c, 1.0f);

    pio_sm_init(pio, sm, offset, &c);
    pio_sm_set_enabled(pio, sm, true);
}

int main() {
    stdio_init_all();

    PIO pio = pio0;
    uint offset = pio_add_program(pio, &detect_pulse_program);

    uint sm_zero = 0;
    uint sm_one  = 1;

    setup_pio_input(pio, sm_zero, offset, GATE0_PIN, ZERO_PIN);
    setup_pio_input(pio, sm_one,  offset, GATE1_PIN,  ONE_PIN);

    while (true) {
        if (!pio_sm_is_rx_fifo_empty(pio, sm_zero)) {
            pio_sm_get_blocking(pio, sm_zero);
            printf("0");
        }
        if (!pio_sm_is_rx_fifo_empty(pio, sm_one)) {
            pio_sm_get_blocking(pio, sm_one);
            printf("1");
        }
    }
}
